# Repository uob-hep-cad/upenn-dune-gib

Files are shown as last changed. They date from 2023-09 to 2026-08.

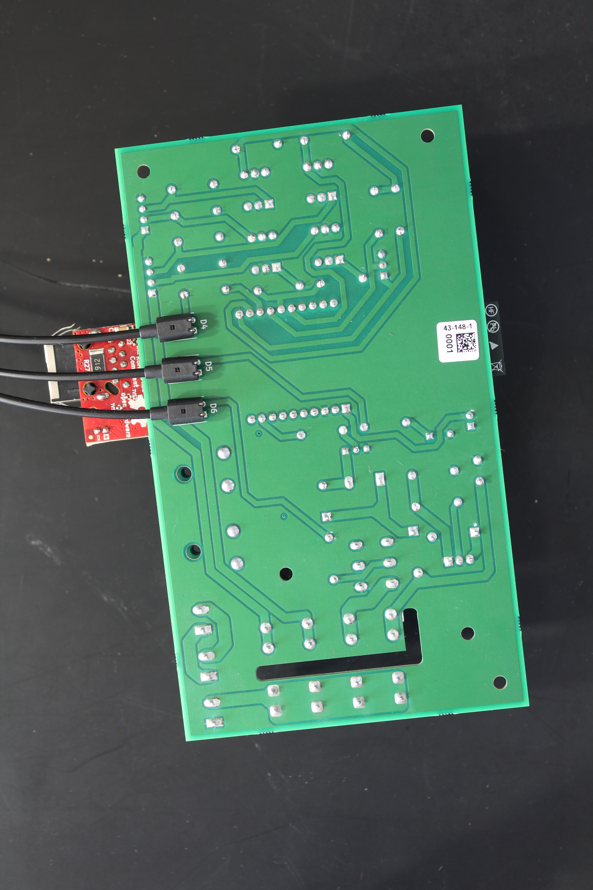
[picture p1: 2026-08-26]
PCB_Health/Photos/IMG_9404.JPG

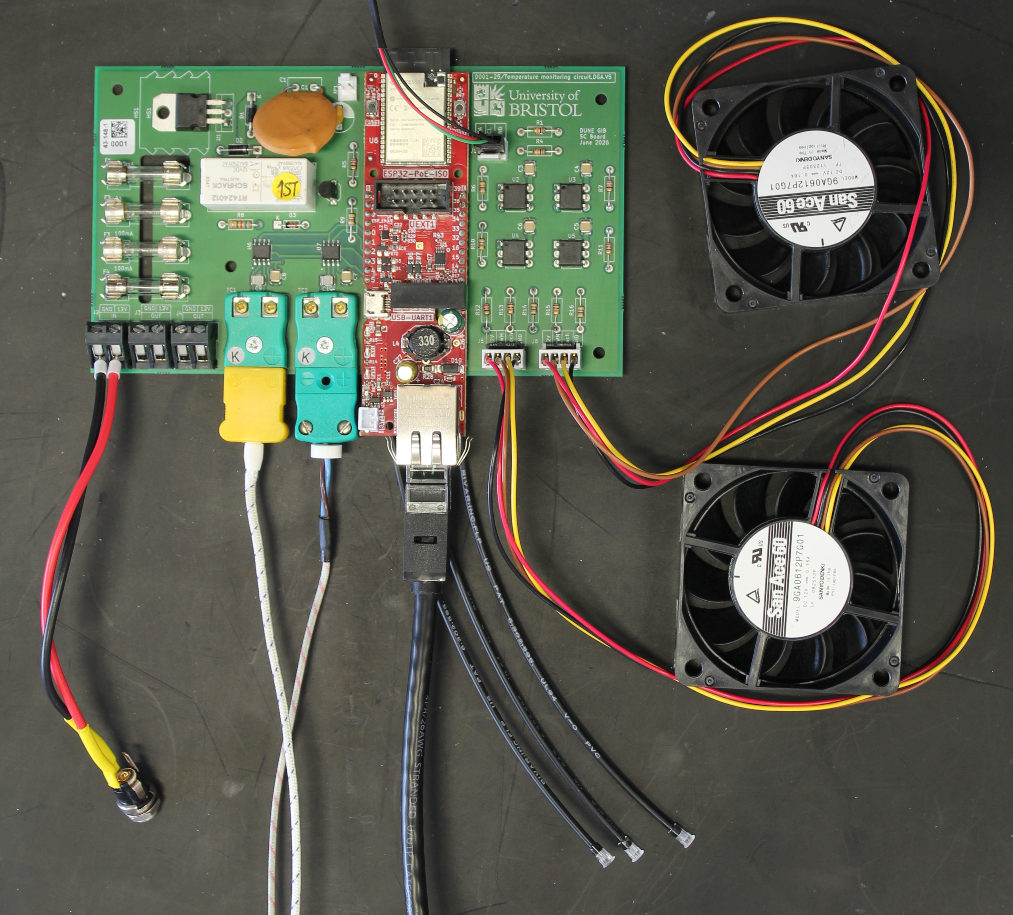
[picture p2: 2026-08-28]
PCB_Health/Photos/IMG_9411_with_cables_cropped.JPG

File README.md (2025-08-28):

# DUNE Timing System GPS Interface Board (GIB) Hardware – PCB Designs

This repository contains hardware design files for DUNE Timing System GPS Interface Board (GIB)  
It includes both Cadence Allegro and KiCAD projects for different components.

---

## 📂 Repository Structure

### `allegro/`
- Contains Cadence Allegro PCB design files.  
- Used for [describe subsystem / purpose here].

### `PCB_Health/`
- KiCAD project for a small **health monitoring board**.  
- Functions:
  - Monitor **fans** and **temperature sensors**
  - Control **power rails** 
- Supports the main GIB.

---

## 🔧 Requirements

To open and work with the files, you’ll need:

- **Cadence Allegro** (for files in `allegro/`)
- **KiCAD (≥ 6.0)** (for files in `PCB_Health/`)

---

## ⚡ Getting Started

1. Clone the repository:
   ```bash
   git clone https://github.com/uob-hep-cad/upenn-dune-gib.git
	cd upenn-dune-gib
2. For the main GIB board, open the `.opj` file with Cadence Capture CIS
3. For the PCB_Health board, open the `.kicad_pro` file with KiCAD

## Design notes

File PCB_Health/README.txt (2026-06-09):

Manufacturing files for DUNE Timing System GIB Slow Control Board
( PCB_Health.v5 )

Files produced with KiCAD 10.0

David.Cussans@bristol.ac.uk , 9/June/26
 
Directory with Gerber artwork: Gerber.D001-25.DGA.V5 
Component placement (CSV and Gerber): PCB_Health.V5-all-pos.csv PCB_Health.V5-pnp_top.gbr PCB_Health.V5-pnp_bottom.gbr

BoM: PCB_Health.V5_BOM.xlsx

4-layer board. FR4. 1.6mm  Newbury Electronics "PCB train" stack-up

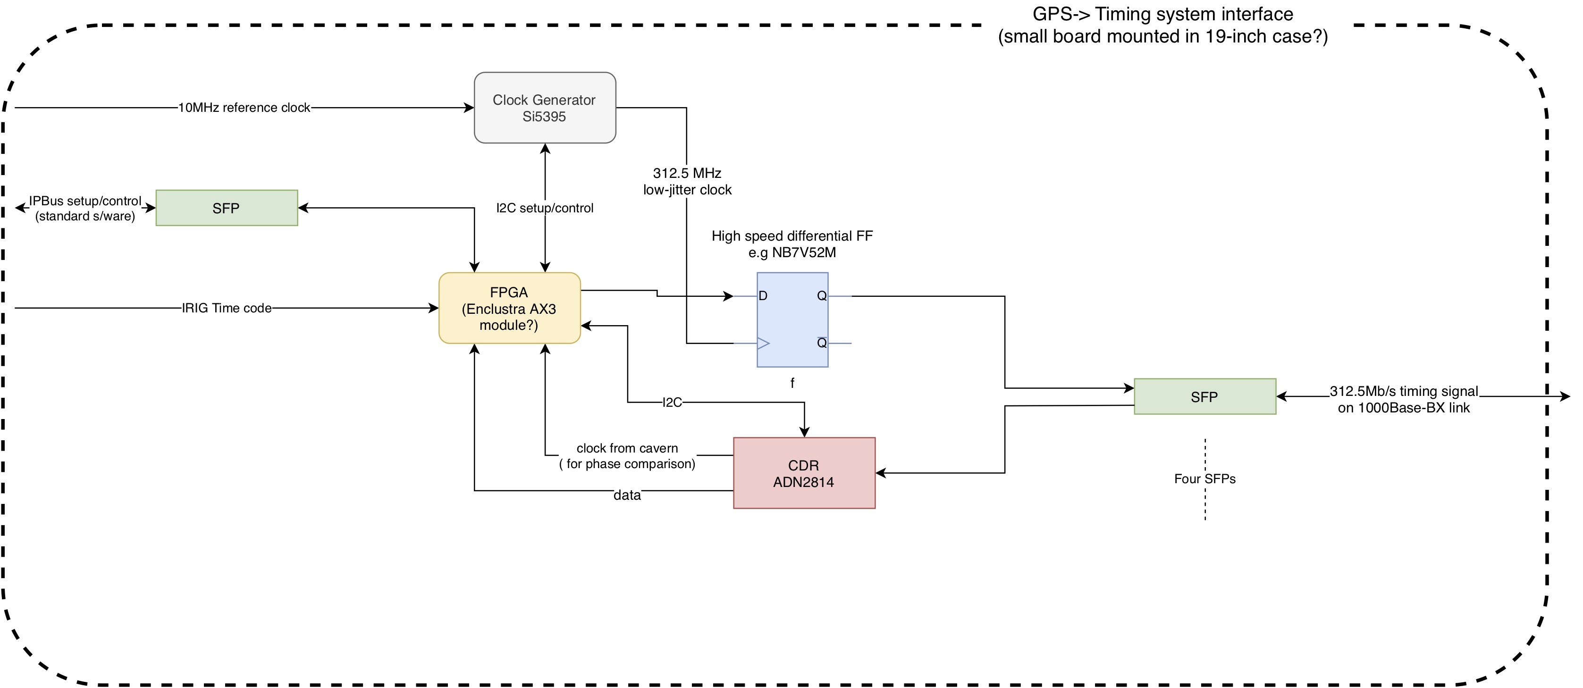
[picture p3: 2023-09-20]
Figures/GPS_timing_system_Interface.jpg

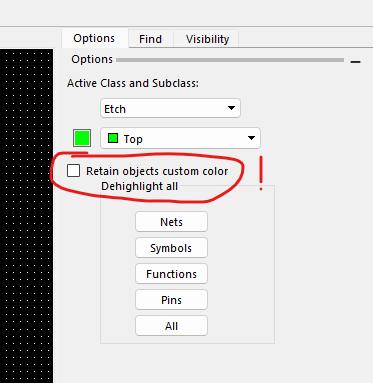
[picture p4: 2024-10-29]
Screenshot 2024-10-08 140926.png

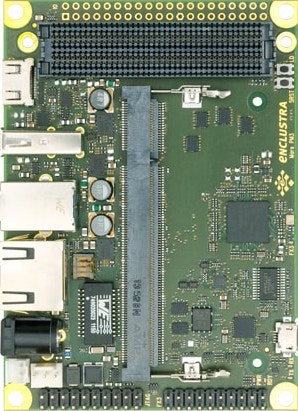
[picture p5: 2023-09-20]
Figures/mars_pm3_top.jpg

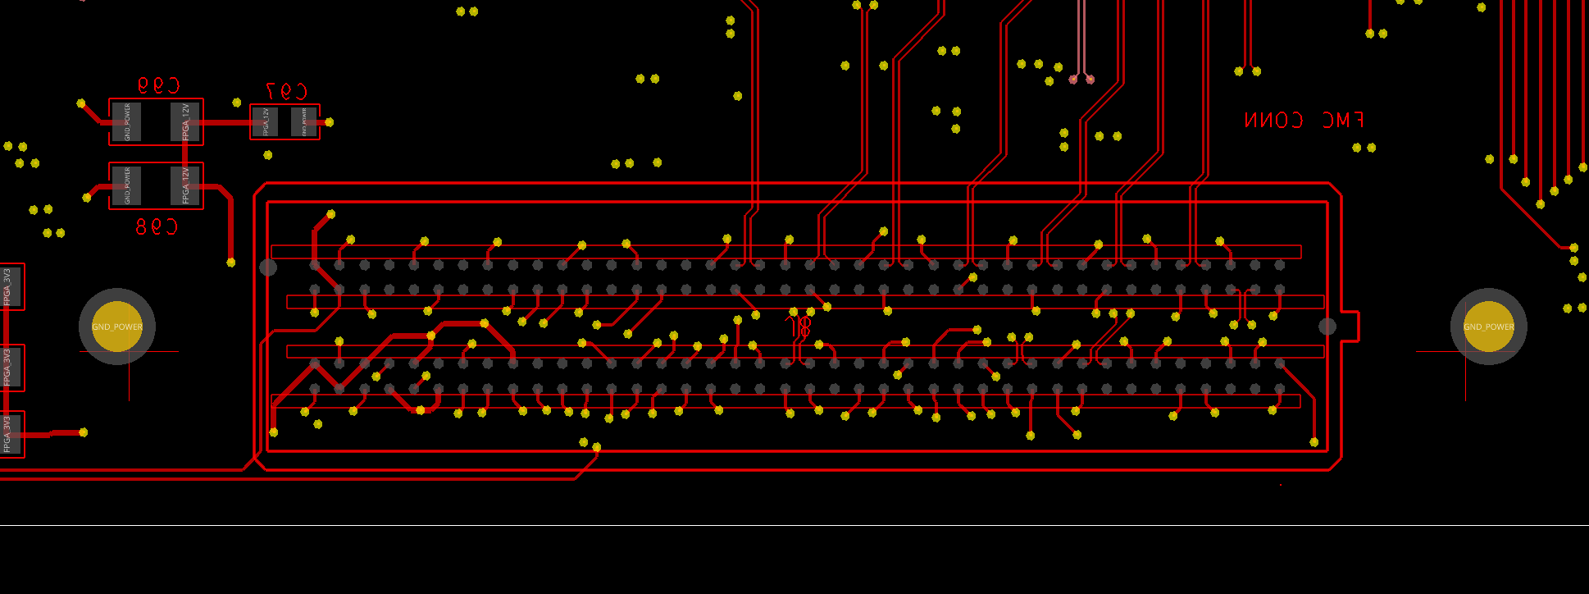
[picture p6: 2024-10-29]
Screenshot 2024-09-06 082252.png

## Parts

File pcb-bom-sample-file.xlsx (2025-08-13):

Item# | Description | Quantity | Manufacturer Name | Manufacturer Part Number | Supplier Name | Supplier Part Number | Designator | Notes
1 | CAP 1nF 16V ±5% 0201 (0603 Metric) Thickness 0.33mm SMD | 12 | Multicomp | MC0201B102K160CT | Farnell | 2320754 | C1-6, C10-15
2 | ICHAUS 3A 6CHANNEL LASER SWITCH | 3 | IC Haus | Ic-HG QFN28 | Free issued | Ic-HG QFN28 | U5, U2008, U3008
3 | 17V Input, 1A Synchronous Step-Down Converter Module in MicroSiP | 5 | Texas Instruments | TPS82150SILT | Mouser | 595-TPS82150SILT | U17, U2004, U3004-3006
Notes / colour key:
 | Quantity, Designator, Manufacturer Name, and Manufacturer Part Number columns are compulsory please.
 | Only the Manufacturer Name and Manufacturer Part Number will be used for costings and subsquent materials procurement.
 | Supplier Name and Supplier Part Number will only be used for costings and subsequent materials procurement should this be marked as critical by the client.
 | Please note that the Description field will NOT be checked during costings and subsequent materials procurement.
 | Item# / Notes column where useful / applicable. Not compulsory.
Formatting / order of columns not critical.

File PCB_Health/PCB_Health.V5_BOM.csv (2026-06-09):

Reference | Qty | Value | DNP | Exclude from BOM | Exclude from Board | Footprint | Description | Datasheet
A1 | 1 | ESP32_POE |  |  |  | ESP32:ESP32-POE-ISO-WROVER | ESP32-POE-ISO-WROVER | https://cdn-learn.adafruit.com/downloads/pdf/adafruit-huzzah32-esp32-feather.pdf
C1 | 1 | 100n |  |  |  | Capacitor_THT:C_Disc_D9.0mm_W5.0mm_P5.00mm | Capacitor THT : C Disc D9.0mm W5.0mm P5.00mm 100n
C2 | 1 | 1u |  |  |  | Capacitor_THT:CP_Radial_D8.0mm_P5.00mm | Capacitor THT : CP Radial D8.0mm P5.00mm 1u
C3,C4,C5,C6,C7,C8 | 6 | 100n |  |  |  | Capacitor_SMD:C_1210_3225Metric | Capacitor SMD : C 1210 3225Metric 100n
C9,C10 | 2 | 10n |  |  |  | Capacitor_SMD:C_1210_3225Metric | Capacitor SMD : C 1210 3225Metric 10n
D1,D2 | 2 | 1N4001 |  |  |  | Diode_THT:D_DO-41_SOD81_P10.16mm_Horizontal | Diode THT : D DO-41 SOD81 P10.16mm Horizontal 1N4001 | http://www.vishay.com/docs/88503/1n4001.pdf
D3 | 1 | 1N4148 |  |  |  | Diode_THT:D_DO-35_SOD27_P7.62mm_Horizontal | Diode THT : D DO-35 SOD27 P7.62mm Horizontal 1N4148 | https://assets.nexperia.com/documents/data-sheet/1N4148_1N4448.pdf
D4,D5,D6 | 3 | LED |  |  |  | Library:FLPR60SG | FLPR60SG
F1 | 1 | 500mA |  |  |  | Library:Littelfuse 100 Spring Brass, PCB Fuse Clip for 5 x 20 mm Cartridge Fuse | Littelfuse 100 Spring Brass, PCB Fuse Clip for 5 x 20 mm Cartridge Fuse 500mA
F2 | 1 | 2A |  |  |  | Library:Littelfuse 100 Spring Brass, PCB Fuse Clip for 5 x 20 mm Cartridge Fuse | Littelfuse 100 Spring Brass, PCB Fuse Clip for 5 x 20 mm Cartridge Fuse 2A
F3,F4 | 2 | 100mA |  |  |  | Library:Littelfuse 100 Spring Brass, PCB Fuse Clip for 5 x 20 mm Cartridge Fuse | Littelfuse 100 Spring Brass, PCB Fuse Clip for 5 x 20 mm Cartridge Fuse 100mA
H1,H2,H4,H5 | 4 | MountingHole |  |  |  | MountingHole:MountingHole_3.2mm_M3 | MountingHole : MountingHole 3.2mm M3
HS1 | 1 | Heatsink |  |  |  | Heatsink:Heatsink_AAVID_TV5G_TO220_Horizontal | Heatsink : Heatsink AAVID TV5G TO220 Horizontal
J1 | 1 | Conn_01x03_Socket |  |  |  | Connector_PinHeader_2.54mm:PinHeader_1x03_P2.54mm_Vertical | Connector PinHeader 2.54mm : PinHeader 1x03 P2.54mm Vertical
J2,J3,J4 | 3 | Conn_01x02_Socket |  |  |  | TerminalBlock:TerminalBlock_Altech_AK300-2_P5.00mm | TerminalBlock : TerminalBlock Altech AK300-2 P5.00mm
J5 | 1 | Conn_01x04_Socket |  |  |  | Library:Mole_KK_1x04__Vertical | Molex KK 1x04 Vertical
J6 | 1 | Conn_01x04_Socket |  |  |  | Connector_PinHeader_2.54mm:PinHeader_1x04_P2.54mm_Vertical | Connector PinHeader 2.54mm : PinHeader 1x04 P2.54mm Vertical
JP1 | 1 | Jumper_2_Open |  |  |  | Connector_PinHeader_2.54mm:PinHeader_1x02_P2.54mm_Vertical | Connector PinHeader 2.54mm : PinHeader 1x02 P2.54mm Vertical
K1 | 1 | RT424012 |  |  |  | Relay_THT:Relay_DPDT_Schrack-RT2-FormC_RM5mm | Relay THT : Relay DPDT Schrack-RT2-FormC RM 5mm | http://www.te.com/commerce/DocumentDelivery/DDEController?Action=showdoc
Q1 | 1 | BC337 |  |  |  | Package_TO_SOT_THT:TO-92_Inline_Wide | Package TO SOT THT : TO-92 Inline Wide BC337 | https://diotec.com/tl_files/diotec/files/pdf/datasheets/bc337.pdf
R1,R4,R13,R15 | 4 | 10k |  |  |  | Library:R_Axial_DIN0207_L6.3mm_D2.5mm_P10.16mm_Horizontal | R Axial DIN0207 L6.3mm D2.5mm P10.16mm Horizontal 10k
R2 | 1 | 220 |  |  |  | Library:R_Axial_DIN0207_L6.3mm_D2.5mm_P10.16mm_Horizontal | R Axial DIN0207 L6.3mm D2.5mm P10.16mm Horizontal
R3 | 1 | 680 |  |  |  | Library:R_Axial_DIN0207_L6.3mm_D2.5mm_P10.16mm_Horizontal | R Axial DIN0207 L6.3mm D2.5mm P10.16mm Horizontal
R5,R7,R11,R12 | 4 | 270 |  |  |  | Library:R_Axial_DIN0207_L6.3mm_D2.5mm_P10.16mm_Horizontal | R Axial DIN0207 L6.3mm D2.5mm P10.16mm Horizontal
R6,R9,R10,R14,R16 | 5 | 470 |  |  |  | Library:R_Axial_DIN0207_L6.3mm_D2.5mm_P10.16mm_Horizontal | R Axial DIN0207 L6.3mm D2.5mm P10.16mm Horizontal
R8 | 1 | 620 |  |  |  | Library:R_Axial_DIN0207_L6.3mm_D2.5mm_P10.16mm_Horizontal | R Axial DIN0207 L6.3mm D2.5mm P10.16mm Horizontal
TC1,TC2 | 2 | Thermocouple_Alt |  |  |  | Connector Thermo:Thermocouple Connector | Connector Thermo : Thermocouple Connector
U1 | 1 | LM317_TO-220 |  |  |  | Package_TO_SOT_THT:TO-220-3_Vertical | Package TO SOT THT : TO-220-3 Vertical | http://www.ti.com/lit/ds/symlink/lm317.pdf
U2,U3,U4,U5 | 4 | H11L1 |  |  |  | Library:DIP-6_W7.62mm | DIP-6 W7.62mm | https://www.onsemi.com/pub/Collateral/H11L3M-D.PDF
U6,U7 | 2 | MAX6675ISA_ |  |  |  | MAX6675ISA_:SOIC127P600X175-8N | MAX6675ISA : SOIC127P600X175-8N

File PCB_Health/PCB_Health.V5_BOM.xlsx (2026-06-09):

Description | Qty per BOM | Quantity per batch | Min Quantity to order | Manufacturer | Manufacturer Part Number | Supplier | Supplier Part Number | Designator | Package Type | Technology | Comment | Status | Original Manufacturer Part No from client BOM
ESP32-POE IOT EVAL BOARD | 1 | 2 | 2 | Olimex LTD | ESP32-POE-ISO-WROVER | DIGIKEY | 1188-ESP32-POE-ISO-WROVER-ND | A1 | Bulk | THT |  | Found | ESP32_POE
CAP CER 0.1UF 500V Z5V RADIAL | 7 | 14 | 14 | Vishay Beyschlag/Draloric/BC Components | S104Z93Z5VL83L0R | DIGIKEY | BC5183-ND | C1,C3,C4,C5,C6,C7,C8 | Bulk | THT |  | Found | 100n
CAP TANT 1UF 10% 25V RADIAL | 1 | 2 | 2 | KEMET | T356A105K025AT | DIGIKEY | 399-3603-ND | C2 | Bulk | THT |  | Found | 1u
YAGEO - CC1210FKNPO9BN103 - SMD Multilayer Ceramic Capacitor, 0.01 µF, 50 V, 1210 [3225 Metric], ± 1%, C0G / NP0 | 2 | 4 | 5 | YAGEO | CC1210FKNPO9BN103 | FARNELL | 4255887 | C9,C10 | Cut Tape | SMD |  | Found | 10n
MULTICOMP PRO - 1N4001. - DIODE, STANDARD RECOVERY, 1A, 50V, DO-204AL-2 | 2 | 4 | 5 | MULTICOMP PRO | 1N4001. | FARNELL | 2306346 | D1,D2 | Cut Tape | THT |  | Found | 1N4001
MULTICOMP PRO - 1N4148. - DIODE, ULTRAFAST RECOVERY, 150mA, 75V, DO-204AH-2 | 1 | 2 | 5 | MULTICOMP PRO | 1N4148. | FARNELL | 2306361 | D3 | Cut Tape | THT |  | Found | 1N4148
LED CBI 3MM GRN THROUGH HOLE | 3 | 6 | 6 | Bivar Inc. | FLPR6.0-SG | DIGIKEY | 492-1201-ND | D4,D5,D6 | Bag | THT |  | Found | LED
FUSE CLIP CARTRIDGE 250V 10A PCB | 1 | 2 | 2 | Littelfuse Inc. | 01000056Z | DIGIKEY | F3784-ND | F1 | Bulk | THT |  | Found | 500mA
FUSE CLIP CARTRIDGE 250V 10A PCB | 1 | 2 | 2 | Littelfuse Inc. | 01000056Z | DIGIKEY | F3784-ND | F2 | Bulk | THT |  | Found | 2A
FUSE CLIP CARTRIDGE 250V 10A PCB | 2 | 4 | 4 | Littelfuse Inc. | 01000056Z | DIGIKEY | F3784-ND | F3,F4 | Bulk | THT |  | Found | 100mA
BOYD - TV5G - Heat Sink, PCB, Board Level, 21.6 °C/W, TO-126, 22 mm, 19 mm, 19 mm | 1 | 2 | 2 | BOYD | TV5G | FARNELL | 170072 | HS1 | Each | UNMOUNTED |  | Found | Heatsink
Headers & Wire Housings 3C STR HEADER W/FRLK | 1 | 2 | 2 | Molex | 22-27-2031 | MOUSER | 538-22-27-2031 | J1 | Standard Pack Qty | THT |  | Found | Conn_01x03_Socket
Fixed Terminal Blocks AK300/2 PC 45DegGry | 3 | 6 | 6 | Altech | 30.602 | MOUSER | 845-30.602 | J2,J3,J4 | Standard Pack Qty | THT |  | Found | Conn_01x02_Socket
MOLEX - 171856-4004 - Pin Header, Black, Board-to-Board, Power, Signal, Wire-to-Board, 2.54 mm, 1 Rows, 4 Contacts | 2 | 4 | 4 | MOLEX | 171856-4004 | FARNELL | 4667772 | J5,J6 | Cut Tape | THT |  | Found | Conn_01x04_Socket
Conn Wire to Board HDR 2 POS 2.54mm Solder ST Top Entry Thru-Hole KK Bag | 1 | 2 | 2 | Molex | 0022232021 | ARROW | 0323_00039992 | JP1 | BAG | THT |  | Found | Jumper_2_Open
Power Relay 12VDC 8A DPDT(29x12.7x15.7)mm THT | 1 | 2 | 2 | TE Connectivity | RT424012 | ARROW | 0323_00028596 | K1 | BOX | THT |  | Found | RT424012
MULTICOMP PRO - BC337 - Bipolar (BJT) Single Transistor, NPN, 45 V, 800 mA, 625 mW, TO-92, Through Hole | 1 | 2 | 5 | MULTICOMP PRO | BC337 | FARNELL | 1574379 | Q1 | Each | THT |  | Found | BC337
MULTICOMP PRO - MCRE000049 - Through Hole Resistor, 10 kohm, MC CFR Series, 125 mW, ± 5%, Axial Leaded, 200 V | 4 | 8 | 8 | MULTICOMP PRO | MCRE000049 | FARNELL | 1700251 | R1,R4,R13,R15 | Each | THT |  | Found | 10k
MULTICOMP PRO - MCRE000029 - Through Hole Resistor, 220 ohm, MC CFR Series, 125 mW, ± 5%, Axial Leaded, 200 V | 1 | 2 | 5 | MULTICOMP PRO | MCRE000029 | FARNELL | 1700228 | R2 | Each | THT |  | Found | 220
MULTICOMP PRO - MCRE000035 - Through Hole Resistor, 680 ohm, MC CFR Series, 125 mW, ± 5%, Axial Leaded, 200 V | 1 | 2 | 5 | MULTICOMP PRO | MCRE000035 | FARNELL | 1700234 | R3 | Each | THT |  | Found | 680
MULTICOMP PRO - MCRE000030 - Through Hole Resistor, 270 ohm, MC CFR Series, 125 mW, ± 5%, Axial Leaded, 200 V | 4 | 8 | 8 | MULTICOMP PRO | MCRE000030 | FARNELL | 1700229 | R5,R7,R11,R12 | Each | THT |  | Found | 270
MULTICOMP PRO - MCRE000033 - Through Hole Resistor, 470 ohm, MC CFR Series, 125 mW, ± 5%, Axial Leaded, 200 V | 5 | 10 | 10 | MULTICOMP PRO | MCRE000033 | FARNELL | 1700232 | R6,R9,R10,R14,R16 | Each | THT |  | Found | 470
RES 620 OHM 5% 1/4W AXIAL | 1 | 2 | 2 | KOA Speer Electronics, Inc. | CF1/4CT52R621J | DIGIKEY | 2019-CF1/4CT52R621JCT-ND | R8 | Cut Tape (CT) | THT |  | Found | 620
LABFACILITY - IM-K-PCB - Thermocouple Connector, Miniature, Green, Socket, Type K, IEC, PCB Mount | 2 | 4 | 4 | LABFACILITY | IM-K-PCB | FARNELL | 3810628 | TC1,TC2 | Each | THT |  | Found | Thermocouple_Alt
Standard Regulator Pos 1.2V to 37V 0.4A 3-Pin(3+Tab) TO-220AB Tube | 1 | 2 | 2 | STMicroelectronics | LM317T | ARROW | 0323_00031097 | U1 | RAIL | THT |  | Found | LM317_TO-220
Optocoupler Logic-Out DC-IN 1-CH 6-Pin DIP | 4 | 8 | 8 | Everlight Electronics | H11L1 | ARROW | 0323_02418914 | U2,U3,U4,U5 | BULK | THT |  | Found | H11L1
ANALOG DEVICES - MAX6675ISA+ - Temperature Sensor IC, Digital, ± 3°C, 0 °C, 1024 °C, NSOIC, 8 Pins | 2 | 4 | 4 | ANALOG DEVICES | MAX6675ISA+ | FARNELL | 2518704 | U6,U7 | Each | SMD |  | Found | MAX6675ISA_

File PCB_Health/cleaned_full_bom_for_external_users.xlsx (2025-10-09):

Description | Qty per BOM | Quantity per batch | Min Quantity to order | Manufacturer | Manufacturer Part Number | Supplier | Supplier Part Number | Designator | Package Type | Technology | Comment | Status | Original Manufacturer Part No from client BOM
WiFi Development Tools - 802.11 ESP32-POE-ISO IoT development board with 100Mb Ethernet, Power over Ethernet, WiFi, BLE, programmer | 1 | 2 | 2 | Olimex Ltd. | ESP32-POE-ISO-WROVER | MOUSER | 909-P32POEISOWROVER | A1 | Standard Pack Qty | THT | ESP32_POE | Found | ESP32-POE-ISO-WROVER
Multilayer Ceramic Capacitors MLCC - SMD/SMT WCAP-CSGP 0.01uF 1210 5% 50V MLCC | 2 | 4 | 4 | Wurth Elektronik | 885012009023 | MOUSER | 710-885012009023 | C1,C2 | Cut Tape | SMD | 10n | Found | 885012009023
CAP CER 0.1UF 50V X7R 0805 | 7 | 14 | 14 | KEMET | C0805C104K5RACTU | DIGIKEY | 399-C0805C104K5RACTUCT-ND | C3,C4,C5,C6,C7,C8,C9 | Cut Tape (CT) | SMD | 100n | Found | C0805C104K5RACTU
Aluminium Electrolytic Capacitors - Radial Leaded 1.0UF 250V ELECT NHG RADIAL | 1 | 2 | 2 | Panasonic | ECA-2EHG010 | MOUSER | 667-ECA-2EHG010 | C10 | Standard Pack Qty | SMD | 1u | Found | ECA2EHG010
MULTICOMP PRO - 1N4001. - DIODE, STANDARD RECOVERY, 1A, 50V, DO-204AL-2 | 2 | 4 | 5 | MULTICOMP PRO | 1N4001. | FARNELL | 2306346 | D1,D2 | Cut Tape | THT | 1N4001 | Found | 1N4001-E3/54
PCB MNT FUSEHOLDER 5X20MM | 4 | 8 | 8 | BULGIN LTD | FX0457 | ANGLIA | 138857001 | F1,F2,F3,F4 | Bag | SMD | 500mA | Found | FX0457
Screws & Fasteners PEEK SOCKET HEAD SCREW M3 X 10 | 1 | 2 | 2 | Essentra | 183031070409 | MOUSER | 144-183031070409 | H1 | Standard Pack Qty | UNMOUNTED | Heatsink fixing | Found
BOYD - TV5G - Heat Sink, PCB, Board Level, 21.6 °C/W, TO-126, 22 mm, 19 mm, 19 mm | 1 | 2 | 2 | BOYD | TV5G | FARNELL | 170072 | HS1 | Each | SMD | Heatsink | Found | TV5G
TERMINAL BLOCK 2W | 3 | 6 | 6 | CAMDENBOSS | CTB0502/2 | ANGLIA | 1041430001 | J1,J2,J5 | Bag | THT | Conn_01x02_Socket | Found | 897-0843
Conn Wire to Board HDR 4 POS 2.54mm Solder ST Top Entry Thru-Hole KK Bag | 2 | 4 | 4 | Molex | 0022292041 | ARROW | 0323_00030517 | J3,J4 | BAG | THT | Conn_01x04_Socket | Found | 22-29-2041
Conn Wire to Board HDR 3 POS 2.54mm Solder ST Top Entry Thru-Hole KK Bag | 1 | 2 | 2 | Molex | 0022272031 | ARROW | 0323_00036827 | J6 | BAG | THT | Conn_01x03_Pin | Found | 22-27-2031
Relay: electromagnetic; DPDT; Ucoil: 12VDC; 8A; 8A/250VAC; 8A/30VDC | 1 | 2 | 2 | TE Connectivity | RT424012 | TME | RT424012 | K1 |  | THT | RT424012 | Found | RT424012
TO92 45V 0.8A 0.625W NPN | 1 | 2 | 1000 | INVAC | BC337-25 | ANGLIA | 1517347001 | Q1 | Bag | THT | BC337 | Found | BC337-25 A1
Metal Film Resistors - Through Hole 470 OHM 1/4W 1% | 5 | 10 | 10 | YAGEO | MFR-25FTE52-470R | MOUSER | 603-MFR-25FTE52-470R | R1,R3,R5,R7,R8 | Standard Pack Qty | THT | 470 | Found | MFR-25FTE52-470R
RES 270 OHM 1% 1/4W AXIAL | 4 | 8 | 8 | YAGEO | MFR-25FTE52-270R | DIGIKEY | 13-MFR-25FTE52-270RCT-ND | R2,R4,R6,R9 | Cut Tape (CT) | THT | 270 | Found | MFR-25FTE52-270R
RES 680 OHM 1% 0.6W AXIAL | 1 | 2 | 2 | TE Connectivity Passive Product | LR1F680R | DIGIKEY | A105963CT-ND | R11 | Cut Tape (CT) | SMD | 680 | Found | LR1F680R
IEC TYPE K PCB SOCKET IM-K-PCB | 2 | 4 | 4 | Labfacility Ltd | XE-1109-001 | DIGIKEY | 5425-XE-1109-001-ND | TC1,TC2 | Bag | THT | Thermocouple_Alt | Found | 304-14-320
Optocoupler Logic-Out DC-IN 1-CH 6-Pin DIP | 4 | 8 | 8 | Everlight Electronics | H11L1 | ARROW | 0323_02418914 | U1,U4,U5,U7 | BULK | SMD | H11L1 | Found | H11L1
ANALOG DEVICES - MAX6675ISA+ - Temperature Sensor IC, Digital, ± 3°C, 0 °C, 1024 °C, NSOIC, 8 Pins | 2 | 4 | 4 | ANALOG DEVICES | MAX6675ISA+ | FARNELL | 2518704 | U2,U3 | Each | SMD | MAX6675ISA_ | Found | MAX6675ISA+
IC: voltage regulator; linear,adjustable; 1.2÷37V; 1.5A; TO220-3 | 1 | 2 | 2 | TEXAS INSTRUMENTS | LM317T/NOPB | TME | LM317T/NOPB | U6 |  | THT | LM317_TO-220 | Found | LM317T/NOPB
RES 220 OHM 1% 1/4W AXIAL | 1 | 2 | 2 | YAGEO | MFR-25FTE52-220R | DIGIKEY | 13-MFR-25FTE52-220RCT-ND | R10 | Cut Tape (CT) | THT |  | Found

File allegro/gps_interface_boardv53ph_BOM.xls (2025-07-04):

Quantity | Designator | Description | Manufacturer | Manufacturer Part Number | Supplier 1 | Supplier Part Number 1 | Notes
3 | J27, J28, J29 | KK 0.1in 3 way latching | Molex | 22-23-2031
1 | J300 | Power to the Board MiniFitJr | Molex | 172448-0004
1 | U100 | Switching Voltage Regulator | Analog Devices | LTM8029IYPBF
2 | C1, C3 | 10nF 16V X7R 0402 | Samsung Electronic | CL05B103JO5NNWC |  |  | Can be alternative but match OR exceed dielectric/volt rating | 0.01UF
47 | C14, C15, C18, C19, C20, C23, C24, C25, C26, C27, C28, C34, C35, C36, C37, C38, C39, C108, C109, C110, C111, C112, C113, C128, C129, C140, C141, C163, C164, C186, C187, C209, C210, C232, C233, C255, C256, C272, C276, C277, C2711, C2733, C2734, C2735, C2736, C2737, C2738 | 100nF 16V X7R 0402 | Kemet | C0402C104J4RAC7411 |  |  | Can be alternative but match OR exceed dielectric/volt rating | 0.1UF
1 | C127 | 4.7uF 16V X5R 0402 | KYOCERA AVX | 0402YD475MAT2A |  |  | Can be alternative but match OR exceed dielectric/volt rating | 4.7UF
1 | C2732 | 470nF 16V X7S 0402 | TDK | CGA2B1X7S1C474K050BE |  |  | Can be alternative but match OR exceed dielectric/volt rating | 0.47UF
76 | C5, C6, C8, C11, C53, C54, C56, C58, C59, C60, C62, C64, C69, C71, C72, C74, C75, C78, C79, C83, C84, C86, C115, C116, C117, C119, C123, C132, C133, C135, C136, C138, C155, C156, C158, C159, C161, C178, C179, C181, C182, C184, C201, C202, C204, C205, C207, C224, C225, C227, C228, C230, C247, C248, C250, C251, C253, C270, C271, C2660, C2670, C2690, C2712, C2713, C2714, C2718, C2722, C2723, C2724, C2725, C2726, C2739, C2740, C2741, C2742, C2750 | 100nF 50V X7R 0603 | KYOCERA AVX | KAM15AR71H104KM |  |  | Can be alternative but match OR exceed dielectric/volt rating | 0.1UF
9 | C7, C9, C10, C12, C13, C16, C21, C22, C29 | 10uF 16V X6S 0603 | Murata | GRM188C81C106MA73D |  |  | Can be alternative but match OR exceed dielectric/volt rating | 10UF
8 | C17, C41, C42, C87, C3712, C3713, C3714, C3715 | 1uF 16V X6S 0603 | Murata | GRT188C81C105KE13D |  |  | Can be alternative but match OR exceed dielectric/volt rating | 1UF
2 | C43, C44 | 470nF 16V X7R 0603 | Kemet | C0603C474K4RACTM |  |  | Can be alternative but match OR exceed dielectric/volt rating | 0.47UF
1 | C51 | 5pF 50V C0G 0603 | KYOCERA AVX | 06035A5R0DAT2A |  |  | Can be alternative but match OR exceed dielectric/volt rating | 5.0PF
5 | C57, C65, C76, C85, C2710 | 10nF 16V X7R 0603 | Vishay | VJ0603Y103KXJAC31X |  |  | Can be alternative but match OR exceed dielectric/volt rating | 0.01UF
18 | C139, C162, C185, C208, C231, C254, C2727, C2728, C2729, C2730, C2731, C2743, C2744, C2745, C2746, C2747, C2748, C2749 | 1nF 16V X7R 0603 | KYOCERA AVX | 0603YC102KAT2A |  |  | Can be alternative but match OR exceed dielectric/volt rating | 1000PF
2 | C274, C275 | 4.7uF 16V X7R 0603 | Murata | GRM188Z71C475KE21D |  |  | Can be alternative but match OR exceed dielectric/volt rating | 4.7UF
1 | C40 | 10uF 16V X7R 0805 | TAIYO YUDEN | EMK212BB7106KG-T |  |  | Can be alternative but match OR exceed dielectric/volt rating | 10UF
12 | C49, C50, C52, C55, C61, C63, C70, C73, C77, C80, C2650, C2680 | 47uF 10V X5R 0805 | Murata | GRM21BR61A476ME15L |  |  | Can be alternative but match OR exceed dielectric/volt rating | 47UF
4 | C97, C100, C101, C105 | 100nF 50V X7R 0805 | KYOCERA AVX | 08055C104K4Z4A |  |  | Can be alternative but match OR exceed dielectric/volt rating | 0.1UF
14 | C134, C137, C157, C160, C180, C183, C203, C206, C226, C229, C249, C252, C2717, C2719 | 22uF 16V X5R 0805 | TDK | C2012X5R1C226K125AC |  |  | Can be alternative but match OR exceed dielectric/volt rating | 22UF
6 | L1, L2, L3, L5, L19, L22 | Ferrite Bead 120ohms 100MHz | Laird | LI0805H121R-10 |  |  | Can be alternative but match OR exceed dielectric/volt rating | 120 Ohm@100MHz
1 | C88 | 22uF 16V X7R 1206 | TAIYO YUDEN | EMK316BB7226ML-T |  |  | Can be alternative but match OR exceed dielectric/volt rating | 22UF
7 | C98, C99, C102, C103, C104, C106, C107 | 47uF 16V X5R 1206 | Murata | GRM31CR61C476ME44L |  |  | Can be alternative but match OR exceed dielectric/volt rating | 47UF
1 | F1 | High Inrush Current Withstand, 1206, 30A | Bourns | SF-1206HI400M-2 |  |  |  | 4A
1 | F2 | 1A 1206 Fuse | MultiComp | MP001606 |  |  |  | 0.75A
4 | C66, C67, C81, C82 | 100uF 16V X5R 1210 | Kemet | C1210C107M4PACTU |  |  | Can be alternative but match OR exceed dielectric/volt rating | 100UF
14 | L7, L8, L9, L10, L11, L12, L13, L14, L15, L16, L17, L18, L20, L21 | 4.7 µH, 1.5 ohm, 55 MHz, 220 mA, 1210 | Bourns | CM322522-4R7KL |  |  |  | 4.7 uH
1 | U6 | Switching Voltage Regulator | Analog Devices | LT8645SJV-2
1 | U1 | Clock Buffer | Analog Devices | LTC6957IDD-2#PBF
1 | U15 | Supervisory Circuit | Texas Instruments | TPS3895ADRYR
1 | FL1 | Choke Surface Mount 500 Ohms @ 100 MHz | Murata | DLW5BTM501SQ2L
4 | J11, J12, J15, J16 | 0.1in Pitch 2 pin header | Tyco Connectivity | 826926-2
10 | D1, D15, D17, D21, D25, D29, D33, D37, D41, D43 | Red 0603 LED | LiteOn | LTST-C193KRKT-5A
15 | D2, D4, D5, D6, D7, D8, D14, D16, D20, D24, D28, D32, D36, D40, D42 | Green 0603 LED | LiteOn | LTST-C193KGKT-5A
6 | U22, U26, U30, U34, U38, U42 | Flip-Flops | OnSemi | NB7V52MMNG
3 | U8, U10, U13 | Current & Power Monitors | Analog Devices | LTC2945CUD
5 | U7, U9, U11, U12, U101 | LDO Voltage Regulator High-Current | Texas Instruments | TPS7A8500RGRT
1 | U107 | (D)Encoders, (De)Multiplexers 4.25Gbps | Microchip | SY58608UMG
1 | U104 | Timer | Analog Devices | ADN2814ACPZ
1 | U48 | Clock Synthesizer/Jitter Cleaner | Skyworks | SI5395A-A-GM
2 | Y1, Y2 | MEMS OSC TCXO 50.0000MHZ LVDS | SiTime | SIT5021AI-2DE-25E-50.000000X
1 | P2 | 20 way 0.1in dual row | TE Connectivity | 1-826632-0
1 | P1 | 12 way 0.1in dual row | TE Connectivity | 5-146256-6
19 | R1, R10, R19, R20, R21, R22, R23, R24, R25, R26, R81, R82, R106, R107, R110, R111, R254, R2670, R2694 | 1K 0402 Resistor | Panasonic | ERJ-2RKF1001X |  |  | Can be alternative but 1% if possible | 1k
13 | R31, R35, R131, R152, R173, R194, R215, R236, R1540, R2683, R2689, R2692, R2693, R265 | 100R 0402 Resistor | Panasonic | ERJ-2RKF1000X |  |  | Can be alternative but 1% if possible | 100
28 | R48, R49, R59, R60, R63, R64, R65, R70, R112, R113, R114, R115, R118, R247, R248, R249, R250, R255, R256, R257, R259, R262, R263, R2662, R2665, R2666, R2686, R2687 | 0R 0402 Resistor | Panasonic | ERJ-U020R00X |  |  | Can be alternative but 1% if possible | 0
1 | R78 | 97.6K 0402 Resistor | Panasonic | ERJ-2RKF9762X |  |  | Can be alternative but 1% if possible | 97.6k
1 | R79 | 20K 0402 Resistor | Panasonic | ERJ-2RKF2002X |  |  | Can be alternative but 1% if possible | 20k
3 | R93, R94, R95 | 4.99K 0402 Resistor | Panasonic | ERJ-2RKF4991X |  |  | Can be alternative but 1% if possible | 4.99k
12 | R121, R122, R142, R143, R163, R164, R184, R185, R205, R206, R226, R227 | 6.81K 0402 Resistor | Panasonic | ERJ-2RKF6811X |  |  | Can be alternative but 1% if possible | 6.81k
12 | R123, R126, R144, R147, R165, R168, R186, R189, R207, R210, R228, R231 | 3.83K 0402 Resistor | Panasonic | ERJ-2RKF3831X |  |  | Can be alternative but 1% if possible | 3.83K
29 | R124, R125, R127, R129, R145, R146, R148, R150, R166, R167, R169, R171, R187, R188, R190, R192, R208, R209, R211, R213, R229, R230, R232, R234, R2676, R2677, R2679, R2681, R2688 | 4.7K 0402 Resistor | Panasonic | ERJ-2RKF4701X |  |  | Can be alternative but 1% if possible | 4.7k
3 | R264, R267, R268 | 49.9R 0402 Resistor | Panasonic | ERJ-2RKF49R9X |  |  | Can be alternative but 1% if possible | 49.9
1 | R2650 | 280K 0402 Resistor | Panasonic | ERJ-2RKF2802X |  |  | Can be alternative but 1% if possible | 280 kOhm
2 | R2, R4 | 24.9R 0603 Resistor | Panasonic | ERJ-PA3F24R9V |  |  | Can be alternative but 1% if possible | 24.9 Ohm
5 | R9, R71, R72, R73, R253 | 0R 0603 Resistor | Panasonic | ERJ-3GEY0R00V |  |  | Can be alternative but 1% if possible | 0 Ohm
4 | R11, R12, R15, R16 | 133R 0603 Resistor | Panasonic | ERJ-PA3F1330V |  |  | Can be alternative but 1% if possible | 133
4 | R13, R14, R17, R18 | 68R 0603 Resistor | Panasonic | ERJ-PA3F68R0V |  |  | Can be alternative but 1% if possible | 68
2 | R32, R34 | 75R 0603 Resistor | Panasonic | ERJ-PA3F75R0V |  |  | Can be alternative but 1% if possible | 75 Ohm
1 | R33 | 1K 0603 Resistor | Panasonic | ERJ-PA3F1001V |  |  | Can be alternative but 1% if possible | 1k
1 | R36 | 390K 0603 Resistor | Panasonic | ERJ-PA3F3903V |  |  | Can be alternative but 1% if possible | 390 kOhm
18 | R38, R40, R50, R56, R61, R128, R130, R149, R151, R170, R172, R191, R193, R212, R214, R233, R235, R2660 | 4.99K 0603 Resistor | Panasonic | ERJ-PA3F4992V |  |  | Can be alternative but 1% if possible | 4.99K
1 | R41 | 1M 0603 Resistor | Panasonic | ERJ-PA3F1004V |  |  | Can be alternative but 1% if possible | 1M
1 | R42 | 17.8K 0603 Resistor | Panasonic | ERJ-PA3F1782V |  |  | Can be alternative but 1% if possible | 17.8k
1 | R46 | 12.1K 0603 Resistor | Panasonic | ERJ-PA3F1212V |  |  | Can be alternative but 1% if possible | 12.1K
1 | R47 | 2.32K 0603 Resistor | Panasonic | ERJ-PA3F2321V |  |  | Can be alternative but 1% if possible | 2.32k
22 | R83, R84, R85, R86, R87, R88, R89, R90, R91, R92, R96, R97, R98, R99, R100, R101, R102, R103, R245, R246, R251, R252 | 4.7K 0603 Resistor | Panasonic | ERJ-PA3F4701V |  |  | Can be alternative but 1% if possible | 4.7K
16 | R104, R105, R108, R109, R119, R120, R140, R141, R161, R162, R182, R183, R203, R204, R224, R225 | 49.9R 0603 Resistor | Panasonic | ERJ-PA3F49R9V |  |  | Can be alternative but 1% if possible | 49.9 Ohm
1 | R116 | 100R 0603 Resistor | Panasonic | ERJ-PA3F1000V |  |  | Can be alternative but 1% if possible | 100
17 | R117, R132, R133, R153, R154, R174, R175, R195, R196, R216, R217, R237, R238, R2684, R2685, R2690, R2691 | 200R 0603 Resistor | Panasonic | ERJ-PA3F2000V |  |  | Can be alternative but 1% if possible | 200
1 | R2640 | 143K 0603 Resistor | Panasonic | ERJ-PA3F1433V |  |  | Can be alternative but 1% if possible | 143K
9 | R37, R39, R43, R44, R51, R57, R62, R74, R80 | 75R 0805 Resistor | Panasonic | ERJ-P06F75R0V |  |  | Can be alternative but 1% if possible | 75 Ohm
1 | R45 | 0.005R 0805 Resistor | Bourns | CRF0805-FZ-R005ELF |  |  | Can be alternative but 1% if possible
4 | R52, R54, R2667, R2668 | 0.0047R 0805 Resistor | Panasonic | ERJ-6BWFR047V
2 | R53, R58 | 0.02R 0805 Resistor | Yageo | PE0805FRF470R02L
1 | J8 | Board to Board & Mezzanine Connector | Samtec | ASP-134606-01
1 | U46 | Board Mount Temperature Sensor | Texas Instruments | LM75AIMX/NOPB
1 | U49 | EEPROM 2K 256 X 8 | Microchip | 24AA025E48T-I/SN
1 | U102 | LDO Voltage Regulator | Texas Instruments | TPS74618PQWDRBRQ1
3 | IC1, IC2, U47 | Translation - Voltage Levels Dual Bit | Texas Instruments | SN74LVC2T45DCUR
2 | U52, U53 | I/O Expander | Texas Instruments | TCA9539PWR
1 | U17 | 4-bit Bidirectional Voltage-Level Translator | Texas Instruments | TXB0104QPWRQ1
1 | U18 | Voltage Level Translator | Texas Instruments | TXB0106IPWRQ1
8 | U24, U28, U32, U36, U40, U44, U105, U106 | OR Gate (single) | Texas Instruments | SN74LVC1G32DBVT
10 | Q1, Q3, Q4, Q5, Q6, Q7, Q10, Q11, Q12, Q14 | NCh Logic Level Enhancement Mode FET | OnSemi | BSS138K
1 | U5 | ESD Protection Diodes | Diodes Inc. | DRTR5V0U4S-7
2 | U2, U3 | LVTTL/TTL-to-Differential Converter | Analog Devices | MAX9371ESA+
4 | J1, J4, J5, J6 | BNC Ins R/A PCB Skt 50Ohm Black | TE Connectivity | 5227161-6
1 | J17 | JACK 1PORT 1000 BASE-T PCB | TE Connectivity | 6-2301994-2
7 | J13, J14, J18, J19, J20, J21, J30 | SFP+ Connector - see line below for "cage" | Molex | 74441-0010
7 | J13, J14, J18, J19, J20, J21, J30 | Cage for SFP+ connector above | TE Connectivity | 2227023-1 |  |  | Press fit part
1 | U19 | 8-Channel I2C Switch | Texas Instruments | TCA9548APWR
2 | J100, J101 | RF Coaxial Connector U.FL | Hirose Electric | U.FL-R-SMT(10)
1 | L6 | 3.3uH Inductor 8040 case | Wurth Elektronik | 74437358033
Compulsory columns highlighted in yellow

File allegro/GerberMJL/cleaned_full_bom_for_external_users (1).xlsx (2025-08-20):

Description | Qty per BOM | Quantity per batch | Min Quantity to order | Manufacturer | Manufacturer Part Number | Supplier | Supplier Part Number | Designator | Package Type | Technology | Comment | Status | Original Manufacturer Part No from client BOM
CAPACITOR; 0402; 50V; 10%; X7R; -55+125C | 2 | 6 | 6 |  | 0402-10nF-50V | Newbury free stock | 0402-10nF-50V | C1,C3 |  | SMD |  | Newbury free stock | 0402-10nF-50V
CAPACITOR; 0603; 50V; 10%; X7R; -55+125C | 76 | 228 | 228 |  | 0603-100nF-50V | Newbury free stock | 0603-100nF-50V | C5,C6,C8,C11,C53,C54,C56,C58,C59,C60,C62,C64,C69,C71,C72,C74,C75,C78,C79,C83,C84,C86,C115,C116,C117,C119,C123,C132,C133,C135,C136,C138,C155,C156,C158,C159,C161,C178,C179,C181,C182,C184,C201,C202,C204,C205,C207,C224,C225,C227,C228,C230,C247,C248,C250,C251,C253,C270,C271,C2660,C2670,C2690,C2712,C2713,C2714,C2718,C2722,C2723,C2724,C2725,C2726,C2739,C2740,C2741,C2742,C2750 |  | SMD |  | Newbury free stock | 0603-100nF-50V
MURATA - GRM188R61A106KE69D - SMD Multilayer Ceramic Capacitor, 10 µF, 10 V, 0603 [1608 Metric], ± 10%, X5R | 9 | 27 | 4000 | MURATA | GRM188R61A106KE69D | FARNELL | 4540398 | C7,C9,C10,C12,C13,C16,C21,C22,C29 | Cut Tape | SMD |  | Found | GRM188R61A106KE69D
CAPACITOR; 0402; 25V; 10%; X5R; -55+85C | 37 | 111 | 111 |  | 0402-100nF-25V | Newbury free stock | 0402-100nF-25V | C14,C15,C18,C19,C20,C23,C24,C25,C26,C27,C28,C34,C35,C36,C37,C38,C39,C108,C109,C110,C111,C112,C113,C128,C129,C272,C276,C277,C2711,C2735,C2736,C2737,C2738,C3274,C3276,C3716,C3717 |  | SMD |  | Newbury free stock | 0402-100nF-25V
CAPACITOR; 0603; 25V; 10%; X5R; -55+85C | 8 | 24 | 24 |  | 0603-1uF-25V | Newbury free stock | 0603-1uF-25V | C17,C41,C42,C87,C3712,C3713,C3714,C3715 |  | SMD |  | Newbury free stock | 0603-1uF-25V
CAP CER 10UF 25V X5R 0805 | 1 | 3 | 3 | TDK Corporation | C2012X5R1E106K125AB | DIGIKEY | 445-5984-1-ND | C40 | Cut Tape (CT) | SMD |  | Found | C2012X5R1E106K125AB
CAPACITOR; 0603; 25V; 10%; X7R; -55+125C | 2 | 6 | 6 |  | 0603-470nF-25V | Newbury free stock | 0603-470nF-25V | C43,C44 |  | SMD |  | Newbury free stock | 0603-470nF-25V
Multilayer Ceramic Capacitors MLCC - SMD/SMT 963-MSASL21GBB5476MT RPLCMT PN 10V 47uF X5R 0805 20% | 12 | 36 | 36 | TAIYO YUDEN | LMK212BBJ476MG-T | MOUSER | 963-LMK212BBJ476MG-T | C49,C50,C52,C55,C61,C63,C70,C73,C77,C80,C2650,C2680 | Cut Tape | SMD |  | Found | LMK212BBJ476MG-T
CAP CER 5PF 50V NP0 0603 | 1 | 3 | 3 | KYOCERA AVX | 06035A5R0CAT2A | DIGIKEY | 478-12708-1-ND | C51 | Cut Tape (CT) | SMD | obsolete - replaced with alternative | Found | 06035A5R0CAT2A
CAPACITOR; 0603; 50V; 10%; X7R; -55+125C | 5 | 15 | 15 |  | 0603-10nF-50V | Newbury free stock | 0603-10nF-50V | C57,C65,C76,C85,C2710 |  | SMD |  | Newbury free stock | 0603-10nF-50V
CAP CER 100UF 6.3V X5R 1210 | 4 | 12 | 12 | Murata Electronics | GRM32ER60J107ME20L | DIGIKEY | 490-3390-1-ND | C66,C67,C81,C82 | Cut Tape (CT) | SMD |  | Found | GRM32ER60J107ME20L
CAP CER 22UF 25V X5R 1206 | 1 | 3 | 3 | Murata Electronics | GRT31CR61E226ME01L | DIGIKEY | 490-12451-1-ND | C88 | Cut Tape (CT) | SMD |  | Found | GRT31CR61E226ME01L
CAPACITOR; 0805; 50V; 10%; X7R; -55+125C | 4 | 12 | 12 |  | 0805-100nF-50V | Newbury free stock | 0805-100nF-50V | C97,C100,C101,C105 |  | SMD |  | Newbury free stock | 0805-100nF-50V
Multilayer Ceramic Capacitors MLCC - SMD/SMT 1206 25VDC 47uF 20% X5R 1.6mm | 7 | 21 | 21 | TDK | C3216X5R1E476M160AC | MOUSER | 810-C3216X5R1E476M | C98,C99,C102,C103,C104,C106,C107 | Cut Tape | SMD |  | Found | C3216X5R1E476M160AC
CAPACITOR; 0402; 6.3V; 20%; X5R; -55+85C | 1 | 3 | 3 |  | 0402-4.7uF-6.3V | Newbury free stock | 0402-4.7uF-6.3V | C127 |  | SMD |  | Newbury free stock | 0402-4.7uF-6.3V
CAP CER 22UF 25V X5R 0805 | 14 | 42 | 42 | Murata Electronics | GRT21BR61E226ME13L | DIGIKEY | 490-12389-1-ND | C134,C137,C157,C160,C180,C183,C203,C206,C226,C229,C249,C252,C2717,C2719 | Cut Tape (CT) | SMD |  | Found | GRT21BR61E226ME13L
CAPACITOR; 0603; 50V; 5%; C0G/NP0; -55+125C | 18 | 54 | 54 |  | 0603-1nF-50V | Newbury free stock | 0603-1nF-50V | C139,C162,C185,C208,C231,C254,C2727,C2728,C2729,C2730,C2731,C2743,C2744,C2745,C2746,C2747,C2748,C2749 |  | SMD |  | Newbury free stock | 0603-1nF-50V
CAPACITOR; 0603; 10V; 20%; X5R; -55+85C | 2 | 6 | 6 |  | 0603-4.7uF-10V | Newbury free stock | 0603-4.7uF-10V | C274,C275 |  | SMD |  | Newbury free stock | 0603-4.7uF-10V
CAPACITOR; 0402; 10V; 10%; X5R; -55+85C | 1 | 3 | 3 |  | 0402-470nF-10V | Newbury free stock | 0402-470nF-10V | C3718 |  | SMD |  | Newbury free stock | 0402-470nF-10V
LED RED DIFFUSED 0603 SMD | 10 | 30 | 30 | ams-OSRAM USA INC. | LS Q976-NR-1-0-20-R18 | DIGIKEY | 475-LSQ976-NR-1CT-ND | D1,D15,D17,D21,D25,D29,D33,D37,D41,D43 | Cut Tape (CT) | SMD |  | Found | LS Q976-NR-1-0-20-R18
LED GREEN DIFFUSED 0603 SMD | 15 | 45 | 45 | ams-OSRAM USA INC. | LG Q396-PS-35-0-20-R18 | DIGIKEY | 475-LGQ396-PS-35CT-ND | D2,D4,D5,D6,D7,D8,D14,D16,D20,D24,D28,D32,D36,D40,D42 | Cut Tape (CT) | SMD |  | Found | LG Q396-PS-35-0-20-R18
Surface Mount Fuses 32VAC/DC 4A Fast Acting Chip Fuse | 1 | 3 | 3 | Eaton Electronics | TR/3216FF4-R | MOUSER | 504-TR/3216FF4-R | F1 | Cut Tape | SMD |  | Found | TR/3216FF4-R
FUSE BRD MT 750MA 63VAC/VDC 1206 | 1 | 3 | 3 | Bel Fuse Inc. | 0685T0750-01 | DIGIKEY | 5923-0685T0750-01CT-ND | F2 | Cut Tape (CT) | SMD |  | Found | 0685T0750-01
MURATA - DLW5BTM501SQ2L - COMMON MODE FILTER, 500 OHM, 4A | 1 | 3 | 3 | MURATA | DLW5BTM501SQ2L | FARNELL | 3471204 | FL1 | Cut Tape | SMD |  | Found | DLW5BTM501SQ2L
TEXAS INSTRUMENTS - SN74LVC2T45DCUR - Bus Transceiver, LVC Family, 2 Input, 50 mA, 3.9 ns, 1.65 V to 5.5 V, VSSOP-8 | 3 | 9 | 9 | TEXAS INSTRUMENTS | SN74LVC2T45DCUR | FARNELL | 3006798 | IC1,IC2,U47 | Cut Tape | SMD |  | Found | SN74LVC2T45DCUR
AMP - TE CONNECTIVITY - 5227161-6 - RF / Coaxial Connector, BNC Coaxial, Right Angle Jack, Solder, 50 ohm, Phosphor Bronze | 4 | 12 | 12 | AMP - TE CONNECTIVITY | 5227161-6 | FARNELL | 2452496 | J1,J4,J5,J6 | Each | THT | Obsolete - alternative P/N | Found | 5227161-6
Headers & Wire Housings 2.54MM CLASSIC PCB HDR STRIP | 4 | 12 | 12 | Samtec | TSW-102-07-G-S | MOUSER | 200-TSW10207GS | J11,J12,J15,J16 | Standard Pack Qty | THT |  | Found | TSW-102-07-G-S
MOLEX - 74441-0010 - Pluggable I/O Connector, SFP, SFP+, 20 Contacts, 1 x 1 (Single), Surface Mount Right Angle | 7 | 21 | 21 | MOLEX | 74441-0010 | FARNELL | 1463052 | J13,J14,J18,J19,J20,J21,J30 | Cut Tape | THT |  | Found | 74441-0010
TE CONNECTIVITY - 6-2301994-2 - Modular Connector, RJ45 Jack, 1 x 1 (Port), 8P8C, Cat6, Through Hole Mount | 1 | 3 | 3 | TE CONNECTIVITY | 6-2301994-2 | FARNELL | 3791964 | J17 | Each | THT |  | Found | 6-2301994-2
Conn Wire to Board HDR 3 POS 2.54mm Solder ST Top Entry Thru-Hole KK 254 Bag | 3 | 9 | 9 | Molex | 0022232031 | ARROW | 0323_00036981 | J27,J28,J29 | BAG | THT |  | Found | 0022232031
RF Connectors / Coaxial Connectors U.FL RECEPTACLE SMT GLD M CONT REEL | 2 | 6 | 6 | Hirose Connector | U.FL-R-SMT(10) | MOUSER | 798-U.FL-R-SMT10 | J100,J101 | Cut Tape | SMD |  | Found | U.FL-R-SMT10
Connector: pin strips; pin header; male; PIN: 3; straight; THT; 1x3 | 2 | 6 | 6 | SAMTEC | TSW-103-07-G-S | TME | TSW-103-07-G-S | J102,J118 |  | THT |  | Found | TSW-103-07-G-S
Conn Wire to Board HDR 4 POS 4.2mm Solder RA Side Entry Thru-Hole Mini-Fit Jr Tray | 1 | 3 | 3 | Molex | 1724480004 | ARROW | 0323_08349238 | J300 | PACK | THT |  | Found | 1724480004
Board to Board & Mezzanine Connectors ASP | 1 | 3 | 3 | Samtec | ASP-134606-01 | MOUSER | 200-ASP-134606-01 | J8 | Cut Tape | SMD |  | Found | ASP-134606-01
FERRITE BEAD 120 OHM 0805 1LN | 6 | 18 | 18 | Laird-Signal Integrity Products | LI0805H121R-10 | DIGIKEY | 240-2383-1-ND | L1,L2,L3,L5,L19,L22 | Cut Tape (CT) | SMD |  | Found | LI0805H121R-10
WURTH ELEKTRONIK - 74437358033 - Power Inductor (SMD), 3.3 µH, 8.25 A, Shielded, 20 A, WE-LHMI Series | 1 | 3 | 3 | WURTH ELEKTRONIK | 74437358033 | FARNELL | 3237507 | L6 | Cut Tape | SMD |  | Found | 74437358033
MURATA - LQH32CN4R7M23L - Power Inductor (SMD), 4.7 µH, 450 mA, Unshielded, LQH32CN_23 Series, 1210 [3225 Metric] | 14 | 42 | 42 | MURATA | LQH32CN4R7M23L | FARNELL | 3471296 | L7,L8,L9,L10,L11,L12,L13,L14,L15,L16,L17,L18,L20,L21 | Cut Tape | SMD |  | Found | LQH32CN4R7M23L
MOSFET N-CH 50V 220MA SOT23-3 | 10 | 30 | 30 | onsemi | BSS138K | DIGIKEY | BSS138KCT-ND | Q1,Q3,Q4,Q5,Q6,Q7,Q10,Q11,Q12,Q14 | Cut Tape (CT) | SMD |  | Found | BSS138K
RESISTOR; 0402; 0.0625W; 100ppm; 1%; 50V; -55+125C | 20 | 60 | 60 |  | 0402-1K | Newbury free stock | 0402-1K | R1,R10,R19,R20,R21,R22,R23,R24,R25,R26,R81,R82,R106,R107,R110,R111,R254,R2670,R2694,R3270 |  | SMD |  | Newbury free stock | 0402-1K
RES SMD 24.9 OHM 1% 1/10W 0603 | 2 | 6 | 6 | Panasonic Electronic Components | ERJ-3EKF24R9V | DIGIKEY | P24.9HCT-ND | R2,R4 | Cut Tape (CT) | SMD |  | Found | ERJ-3EKF24R9V
RESISTOR; 0603; 0.1W; 400ppm; ≤50mΩ; 75V; -55+125C | 5 | 15 | 15 |  | 0603-0R | Newbury free stock | 0603-0R | R9,R71,R72,R73,R253 |  | SMD |  | Newbury free stock | 0603-0R
RES SMD 133 OHM 1% 1/10W 0603 | 4 | 12 | 12 | Panasonic Electronic Components | ERJ-3EKF1330V | DIGIKEY | P133HCT-ND | R11,R12,R15,R16 | Cut Tape (CT) | SMD |  | Found | ERJ-3EKF1330V
RESISTOR; 0603; 0.1W; 100ppm; 1%; 75V; -55+125C | 4 | 12 | 12 |  | 0603-68R | Newbury free stock | 0603-68R | R13,R14,R17,R18 |  | SMD |  | Newbury free stock | 0603-68R
RESISTOR; 0402; 0.0625W; 100ppm; 1%; 50V; -55+125C | 5 | 15 | 15 |  | 0402-100R | Newbury free stock | 0402-100R | R31,R35,R1540,R2692,R2693 |  | SMD |  | Newbury free stock | 0402-100R
RESISTOR; 0402; 0.0625W; 200ppm; 1%; 50V; -55+125C | 2 | 6 | 6 |  | 0402-75R | Newbury free stock | 0402-75R | R32,R34 |  | SMD |  | Newbury free stock | 0402-75R
RESISTOR; 0603; 0.1W; 100ppm; 1%; 75V; -55+125C | 1 | 3 | 3 |  | 0603-1K | Newbury free stock | 0603-1K | R33 |  | SMD |  | Newbury free stock | 0603-1K
RESISTOR; 0603; 0.1W; 100ppm; 1%; 75V; -55+125C | 1 | 3 | 3 |  | 0603-390K | Newbury free stock | 0603-390K | R36 |  | SMD |  | Newbury free stock | 0603-390K
RESISTOR; 0805; 0.125W; 100ppm; 1%; 150V; -55+125C | 9 | 27 | 27 |  | 0805-75R | Newbury free stock | 0805-75R | R37,R39,R43,R44,R51,R57,R62,R74,R80 |  | SMD |  | Newbury free stock | 0805-75R
RES 4.99K OHM 1% 1/10W 0603 | 18 | 54 | 54 | Stackpole Electronics Inc | RMCF0603FT4K99 | DIGIKEY | RMCF0603FT4K99CT-ND | R38,R40,R50,R56,R61,R2660,R128,R130,R149,R151,R170,R172,R191,R193,R212,R214,R233,R235 | Cut Tape (CT) | SMD |  | Found | RMCF0603FT4K99
RESISTOR; 0603; 0.1W; 100ppm; 1%; 75V; -55+125C | 1 | 3 | 3 |  | 0603-1M | Newbury free stock | 0603-1M | R41 |  | SMD |  | Newbury free stock | 0603-1M
RES SMD 17.8K OHM 1% 1/10W 0603 | 1 | 3 | 3 | Panasonic Electronic Components | ERJ-3EKF1782V | DIGIKEY | P17.8KHCT-ND | R42 | Cut Tape (CT) | SMD |  | Found | ERJ-3EKF1782V
RES 12.1K OHM 1% 1/10W 0603 | 1 | 3 | 3 | Stackpole Electronics Inc | RMCF0603FT12K1 | DIGIKEY | RMCF0603FT12K1CT-ND | R46 | Cut Tape (CT) | SMD |  | Found | RMCF0603FT12K1
RES 2.32K OHM 1% 1/10W 0603 | 1 | 3 | 3 | Stackpole Electronics Inc | RMCF0603FT2K32 | DIGIKEY | RMCF0603FT2K32CT-ND | R47 | Cut Tape (CT) | SMD |  | Found | RMCF0603FT2K32
RESISTOR; 0402; 0.0625W; 400ppm; ≤50mΩ; 50V; -55+125C | 35 | 105 | 105 |  | 0402-0R | Newbury free stock | 0402-0R | R48,R49,R59,R60,R63,R64,R65,R70,R112,R113,R114,R115,R118,R247,R248,R249,R250,R255,R256,R257,R258,R259,R260,R261,R262,R263,R2661,R2662,R2663,R2664,R2665,R2666,R3696,R3697,R265 |  | SMD |  | Newbury free stock | 0402-0R
RES 0.02 OHM 1% 1/4W 0805 | 7 | 21 | 21 | Stackpole Electronics Inc | CSR0805FK20L0 | DIGIKEY | CSR0805FK20L0CT-ND | R52,R54,R2667,R2668,R53,R58,R2671 | Cut Tape (CT) | SMD | Not available & P/N is wrong. Use 0.02R as a temp bodge | Found | CSR0805FK20L0
RES SMD 97.6K OHM 1% 1/10W 0402 | 1 | 3 | 3 | Panasonic Electronic Components | ERJ-2RKF9762X | DIGIKEY | P97.6KLCT-ND | R78 | Cut Tape (CT) | SMD |  | Found | ERJ-2RKF9762X
RESISTOR; 0402; 0.0625W; 100ppm; 1%; 50V; -55+125C | 1 | 3 | 3 |  | 0402-20K | Newbury free stock | 0402-20K | R79 |  | SMD |  | Newbury free stock | 0402-20K
RESISTOR; 0603; 0.1W; 100ppm; 1%; 75V; -55+125C | 22 | 66 | 66 |  | 0603-4K7 | Newbury free stock | 0603-4K7 | R83,R84,R85,R86,R87,R88,R89,R90,R91,R92,R96,R97,R98,R99,R100,R101,R102,R103,R245,R246,R251,R252 |  | SMD |  | Newbury free stock | 0603-4K7
PANASONIC - ERJ2RKF4991X - SMD Chip Resistor, 4.99 kohm, ± 1%, 100 mW, 0402 [1005 Metric], Thick Film, Precision | 3 | 9 | 10 | PANASONIC | ERJ2RKF4991X | FARNELL | 2059145 | R93,R94,R95 | Cut Tape | SMD |  | Found | ERJ2RKF4991X
Thin Film Resistors - SMD 0603 49.9ohm 0.1% 25ppm | 16 | 48 | 48 | Panasonic | ERA-3AEB49R9V | MOUSER | 667-ERA-3AEB49R9V | R104,R105,R108,R109,R119,R120,R140,R141,R161,R162,R182,R183,R203,R204,R224,R225 | Cut Tape | SMD | Thin film for high freq use | Found | ERA-3AEB49R9V
RESISTOR; 0603; 0.1W; 100ppm; 1%; 75V; -55+125C | 1 | 3 | 3 |  | 0603-100R | Newbury free stock | 0603-100R | R116 |  | SMD |  | Newbury free stock | 0603-100R
RESISTOR; 0603; 0.1W; 100ppm; 1%; 75V; -55+125C | 17 | 51 | 51 |  | 0603-200R | Newbury free stock | 0603-200R | R117,R132,R133,R153,R154,R174,R175,R195,R196,R216,R217,R237,R238,R2684,R2685,R2690,R2691 |  | SMD |  | Newbury free stock | 0603-200R
RESISTOR; 0402; 0.0625W; 100ppm; 1%; 50V; -55+125C | 30 | 90 | 90 |  | 0402-4K7 | Newbury free stock | 0402-4K7 | R124,R125,R127,R129,R145,R146,R148,R150,R166,R167,R169,R171,R187,R188,R190,R192,R208,R209,R211,R213,R229,R230,R232,R234,R2676,R2677,R2679,R2681,R2696,R3698 |  | SMD |  | Newbury free stock | 0402-4K7
RES 143K OHM 1% 1/10W 0603 | 1 | 3 | 3 | Stackpole Electronics Inc | RMCF0603FT143K | DIGIKEY | RMCF0603FT143KCT-ND | R2640 | Cut Tape (CT) | SMD |  | Found | RMCF0603FT143K
RES SMD 280K OHM 1% 1/16W 0402 | 1 | 3 | 3 | Bourns Inc. | CR0402-FX-2803GLF | DIGIKEY | CR0402-FX-2803GLFCT-ND | R2650 | Cut Tape (CT) | SMD |  | Found | CR0402-FX-2803GLF
LTC6957IDD-2#PBF | 1 | 3 | 3 |  | LTC6957IDD-2#PBF | Client |  | U1 |  | SMD | obsolete? Seems various chip-brokers have stock though. | I'll supply | LTC6957IDD-2#PBF
ANALOG DEVICES - MAX9371ESA+ - Translator, LVTTL/TTL-to-Differential LVPECL/PECL, 1 Input, 50 mA, 270 ps, 3 V to 5.25 V, NSOIC-8 | 2 | 6 | 6 | ANALOG DEVICES | MAX9371ESA+ | FARNELL | 2516400 | U2,U3 | Each | SMD | Avoid Digikey - £100 special shipping | Found | MAX9371ESA+
TVS DIODE 5.5VWM SOT363 | 1 | 3 | 3 | Diodes Incorporated | DRTR5V0U4S-7 | DIGIKEY | DRTR5V0U4S-7DICT-ND | U5 | Cut Tape (CT) | SMD |  | Found | DRTR5V0U4S-7
ANALOG DEVICES - LT8645SJV-2#PBF - DC-DC Switching Synchronous Buck Regulator, Adjustable, 3.4V to 64V in, LQFN-EP-32 | 1 | 3 | 3 | ANALOG DEVICES | LT8645SJV-2#PBF | FARNELL | 4407063 | U6 | Each | SMD |  | Found | LT8645SJV-2#PBF
LDO Voltage Regulators High-Current (4 A) L DO Volt Regulator A 595-TPS7A8500RGRR | 5 | 15 | 15 | Texas Instruments | TPS7A8500RGRT | MOUSER | 595-TPS7A8500RGRT | U7,U9,U11,U12,U101 | Cut Tape | SMD |  | Found | TPS7A8500RGRT
ANALOG DEVICES - LTC2945CUD#PBF - Power Monitor, 2.7 V to 80 V in, QFN-EP, 12-Pins, 0 °C to 70 °C | 3 | 9 | 9 | ANALOG DEVICES | LTC2945CUD#PBF | FARNELL | 4028343 | U8,U10,U13 | Each | SMD |  | Found | LTC2945CUD#PBF
IC SUPERVISOR 1 CHANNEL 6SON | 1 | 3 | 3 | Texas Instruments | TPS3895ADRYR | DIGIKEY | 296-29806-1-ND | U15 | Cut Tape (CT) | SMD |  | Found | TPS3895ADRYR
IC XLTR VL BIDIR 14-TSSOP | 1 | 3 | 3 | Texas Instruments | TXB0104QPWRQ1 | DIGIKEY | 296-27760-1-ND | U17 | Cut Tape (CT) | SMD |  | Found | TXB0104QPWRQ1
IC XLTR VL BIDIR 16-TSSOP | 2 | 6 | 6 | Texas Instruments | TXB0106IPWRQ1 | DIGIKEY | 296-24960-1-ND | U18,U347 | Cut Tape (CT) | SMD |  | Found | TXB0106IPWRQ1
TEXAS INSTRUMENTS - TCA9548APWR - Specialized Interface, I2C, SMBus, Servers & Routers, 1.65 V, 5.5 V, TSSOP, 24 Pins | 1 | 3 | 3 | TEXAS INSTRUMENTS | TCA9548APWR | FARNELL | 3124884 | U19 | Cut Tape | SMD |  | Found | TCA9548APWR
IC FF D-TYPE SINGLE 1BIT 16QFN | 6 | 18 | 18 | onsemi | NB7V52MMNG | DIGIKEY | NB7V52MMNGOS-ND | U22,U26,U30,U34,U38,U42 | Tube | SMD |  | Found | NB7V52MMNG
Board Mount Temperature Sensors Digital Temp Sensor & Thermal Watchdog A 926-LM75AIM/NOPB | 1 | 3 | 3 | Texas Instruments | LM75AIMX/NOPB | MOUSER | 926-LM75AIMX/NOPB | U46 | Cut Tape | SMD |  | Found | LM75AIMX/NOPB
Clock Generator 0.008MHz to 750MHz-IN 1028MHz-OUT 64-Pin QFN EP | 1 | 3 | 3 | Skyworks Solutions | SI5395A-A-GM | ARROW | 1762_12545901 | U48 | TRAY | SMD |  | Found | SI5395A-A-GM
EEPROM 2K 256 X 8 1.8V SERIAL EE, IND | 1 | 3 | 3 | Microchip Technology | 24AA025E48T-I/SN | MOUSER | 579-24AA025E48T-I/SN | U49 | Cut Tape | SMD |  | Found | 24AA025E48T-I/SN
IC XPND 400KHZ I2C SMBUS 24TSSOP | 2 | 6 | 6 | Texas Instruments | TCA9539PWR | DIGIKEY | 296-25130-1-ND | U52,U53 | Cut Tape (CT) | SMD |  | Found | TCA9539PWR
ANALOG DEVICES - LTM8029IY#PBF - DC/DC POL Converter, Adjustable, Buck, 4.5 to 36 V in, 1.2 to 18V/0.6A out, BGA-35 | 1 | 3 | 3 | ANALOG DEVICES | LTM8029IY#PBF | FARNELL | 4029530 | U100 | Each | SMD |  | Found | LTM8029IY#PBF
IC REG LINEAR 1.8V 1A 8-SON | 1 | 3 | 3 | Texas Instruments | TPS74618PQWDRBRQ1 | DIGIKEY | 296-TPS74618PQWDRBRQ1CT-ND | U102 | Cut Tape (CT) | SMD |  | Found | TPS74618PQWDRBRQ1
Encoders, Decoders, Multiplexers & Demultiplexers 4.25Gbps 2:1 LVPECL Multiplexer w/ FSI Inputs | 1 | 3 | 3 | Microchip Technology | SY58608UMG | MOUSER | 998-SY58608UMG | U107 | Standard Pack Qty | SMD |  | Found | SY58608UMG
IC CLOCK/DATA RECOVERY 32-LFCSP | 1 | 3 | 3 | Analog Devices Inc. | ADN2818ACPZ | DIGIKEY | ADN2818ACPZ-ND | U110 | Tray | SMD | Hard to get hold of! BoM calls for ADN2817..., fit lower spec ADN2818 instead. | Found | ADN2818ACPZ
IC INVERTER 2CH 2-INP SOT26 | 8 | 24 | 24 | Diodes Incorporated | 74LVC2G04W6-7 | DIGIKEY | 74LVC2G04W6-7DICT-ND | U348,U349,U350,U351,U352,U353,U354,U355 | Cut Tape (CT) | SMD |  | Found | 74LVC2G04W6-7
MEMS OSC TCXO 50.0000MHZ LVDS | 2 | 6 | 6 | SiTime | SIT5021AI-2DE-25E-50.000000X | DIGIKEY | 1473-30178-1-ND | Y1,Y2 | Cut Tape (CT) | SMD |  | Found | SIT5021AI-2DE-25E-50.000000X

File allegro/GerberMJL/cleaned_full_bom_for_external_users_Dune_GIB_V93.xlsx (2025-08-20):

W/Days | 3 Qty | Price breakdown
9 | - |  | Each | Batch | W/Days
10 | - | PCB | £ 617.31 | £ 1851.93 | 5 W/Days
15 | £ 5051.38 | Assembly | £ 619.79 | £ 1859.38 | 10 W/Days
20 | £ 4613.41 | Components | £ 446.69 | £ 1340.07 | 0 W/Days
25 | £ 4445.29 | TOTAL | £ 1683.79 | £ 5051.38 | 15 W/Days
30 | £ 4226.29
45 | £ 3974.11

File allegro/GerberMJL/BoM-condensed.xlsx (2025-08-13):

Item Number | Quantity | Value | Description | Part Number | Part Reference | Manufacturer Part Number | Manufacturer | Distributor Part Number | Distributor | Voltage | Tolerance
1 | 2 | 0.01UF |  | C0402C103K3RACTU | C1,C3 |  |  |  |  | 25V | 10%
2 | 76 | 0.1UF |  | 445-1316-2-ND | C5,C6,C8,C11,C53,C54,C56,C58,C59,C60,C62,C64,C69,C71,C72,C74,C75,C78,C79,C83,C84,C86,C115,C116,C117,C119,C123,C132,C133,C135,C136,C138,C155,C156,C158,C159,C161,C178,C179,C181,C182,C184,C201,C202,C204,C205,C207,C224,C225,C227,C228,C230,C247,C248,C250,C251,C253,C270,C271,C2660,C2670,C2690,C2712,C2713,C2714,C2718,C2722,C2723,C2724,C2725,C2726,C2739,C2740,C2741,C2742,C2750 |  |  |  |  | 25V
3 | 9 | 10UF |  | GRM188R61A106KE69D | C7,C9,C10,C12,C13,C16,C21,C22,C29 |  |  |  |  | 10V | 10%
4 | 37 | 0.1UF |  | 445-7348-2-ND | C14,C15,C18,C19,C20,C23,C24,C25,C26,C27,C28,C34,C35,C36,C37,C38,C39,C108,C109,C110,C111,C112,C113,C128,C129,C272,C276,C277,C2711,C2735,C2736,C2737,C2738,C3274,C3276,C3716,C3717 |  |  |  |  | 25V
5 | 8 | 1UF |  | C1608X7R1E105M080AB | C17,C41,C42,C87,C3712,C3713,C3714,C3715 |  |  |  |  | 25V
6 | 1 | 10UF |  | 445-5984-1-ND | C40 |  |  |  |  | 25V
7 | 2 | 0.47UF |  | CC0603KRX5R8BB474 | C43,C44 |  |  |  |  | 25V | 10%
8 | 12 | 47UF |  | 587-5465-6-ND | C49,C50,C52,C55,C61,C63,C70,C73,C77,C80,C2650,C2680 |  |  |  |  | 10V
9 | 1 | 5.0PF | CAP 5.0PF 50V CERAMIC 0603 SMD | PCC050CVTR-ND | C51 | ECU-V1H050CCV | Panasonic - SCD | PCC050CVTR-ND | Digi-Key | 50V
10 | 5 | 0.01UF |  | C0603C103F3GACTU | C57,C65,C76,C85,C2710 |  |  |  |  | 25V
11 | 4 | 100UF |  | GRM32ER60J107ME20L | C66,C67,C81,C82 |  |  |  |  | 6.3V | 20%
12 | 1 | 22UF |  | GRT31CR61E226ME01L | C88 |  |  |  |  | 25V | 20%
13 | 4 | 0.1UF |  | 445-8173-1-ND | C97,C100,C101,C105 |  |  |  |  | 25V
14 | 7 | 47UF |  | C3216X5R1E476M160AC | C98,C99,C102,C103,C104,C106,C107 |  |  |  |  | 25V | 20%
15 | 1 | 4.7UF |  | GRM155R60J475ME87D | C127 |  |  |  |  | 6.3V
16 | 14 | 22UF |  | GRT21BR61E226ME13L | C134,C137,C157,C160,C180,C183,C203,C206,C226,C229,C249,C252,C2717,C2719 |  |  |  |  | 25V | 20%
17 | 18 | 1000PF | CAP 1000PF 50V CERAMIC 0603 SMD | PCC102BVTR-ND | C139,C162,C185,C208,C231,C254,C2727,C2728,C2729,C2730,C2731,C2743,C2744,C2745,C2746,C2747,C2748,C2749 | ECU-V1H102KBV | Panasonic - SCD | PCC102BVTR-ND | Digi-Key | 50V
18 | 2 | 4.7UF |  | C0603C475M8PACTU | C274,C275 |  |  |  |  | 10V | 20%
19 | 1 | 0.47UF |  | GRM155R60J474KE19J | C3718 |  |  |  |  | 6.3V
20 | 1 | RED |  | LS L296-P2Q2-1-Z | D1
21 | 15 | GREEN |  | LG Q396-PS-35 | D2,D4,D5,D6,D7,D8,D14,D16,D20,D24,D28,D32,D36,D40,D42
22 | 9 | RED |  | LS Q976-NR-1 | D15,D17,D21,D25,D29,D33,D37,D41,D43
23 | 1 | 4A |  | TR/3216FF4-R | F1
24 | 1 | 0.75A |  | 0685T0750-01 | F2
25 | 1 | 120 Ohm@100MHz |  | DLW5BTM501SQ2L | FL1
26 | 3 | SN74LVC2T45DCU |  | SN74LVC2T45DCU | IC1,IC2,U47
27 | 4 | BNC/R |  | 1-1634612-0 | J1,J4,J5,J6
28 | 4 | HDR1x2 |  | HDR1x2 | J11,J12,J15,J16
29 | 7 | 0744410010 |  | 0744410010 | J13,J14,J18,J19,J20,J21,J30
30 | 1 | 6-2301994-2 |  | 6-2301994-2 | J17
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

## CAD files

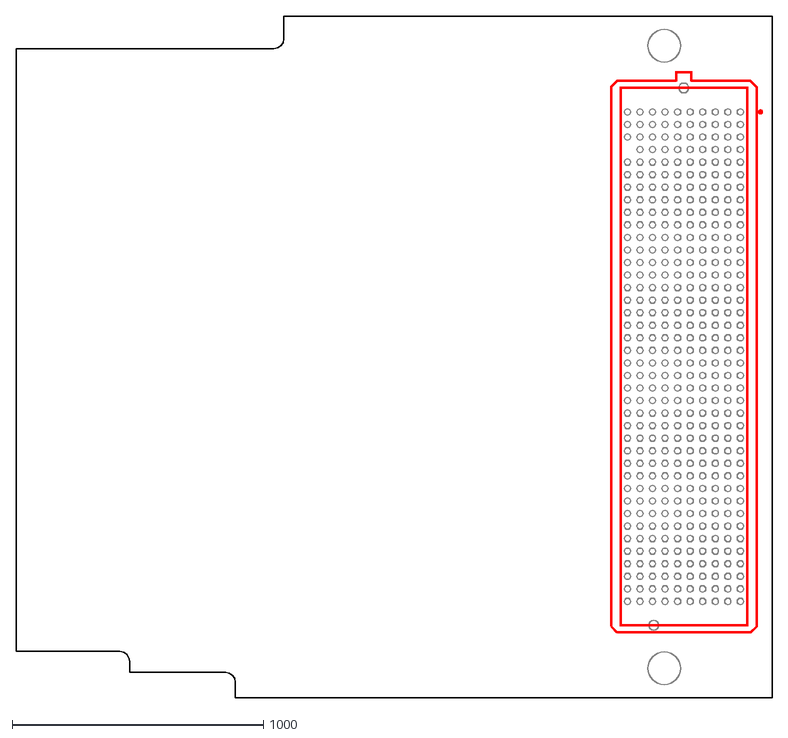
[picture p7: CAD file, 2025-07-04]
allegro/dune_outline.dxf
3011.8 x 2716.5

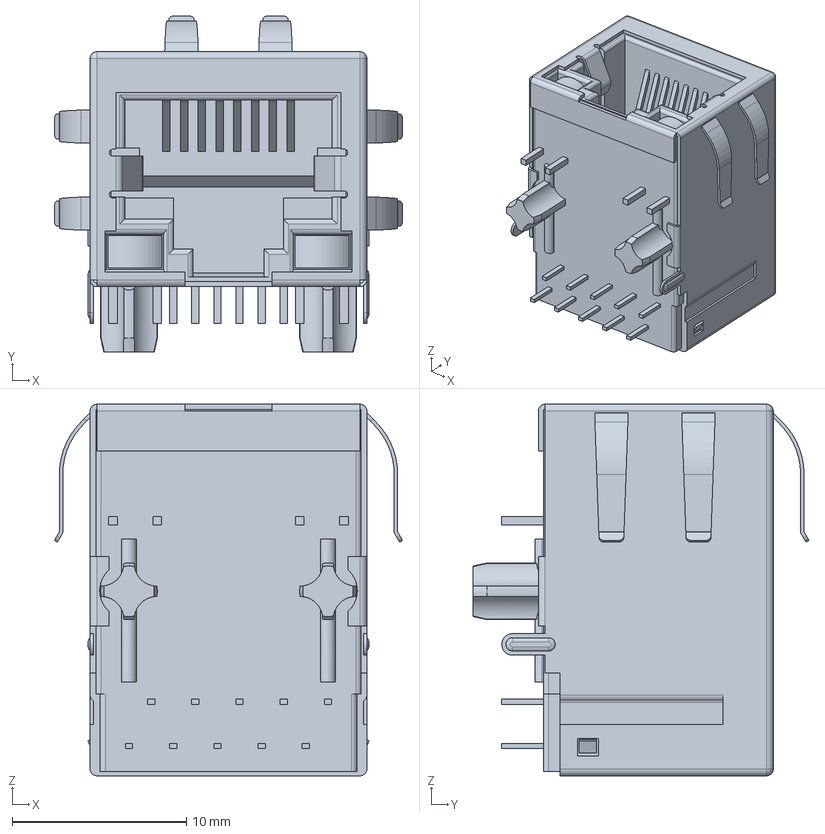
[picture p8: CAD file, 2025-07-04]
allegro/exp_sym/6-2301994-2.stp
20.0 x 19.3 x 21.4 mm

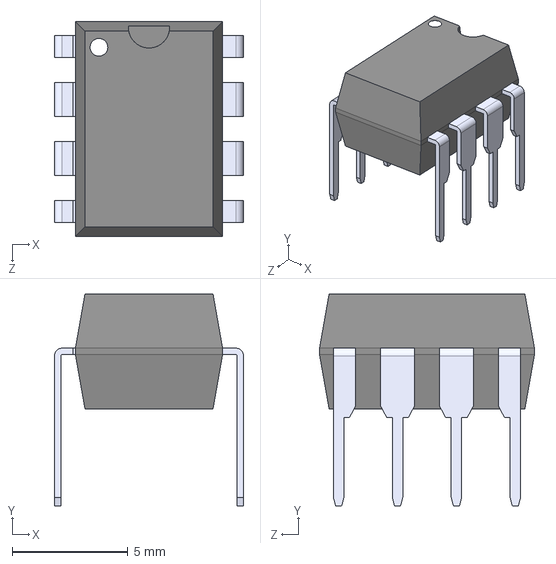
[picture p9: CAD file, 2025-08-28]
PCB_Health/LT1025CN8_PBF/LT1025CN8_PBF.step
8.15 x 9.14 x 9.27 mm

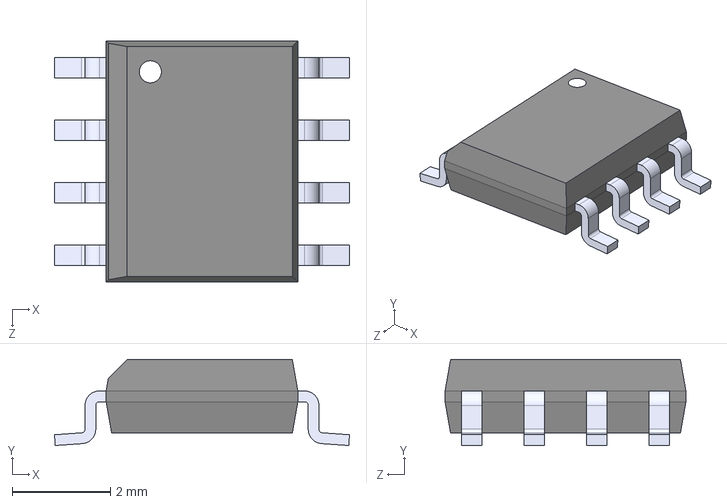
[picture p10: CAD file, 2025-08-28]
PCB_Health/MAX6675ISA_/MAX6675ISA_.step
6.00 x 1.75 x 4.90 mm

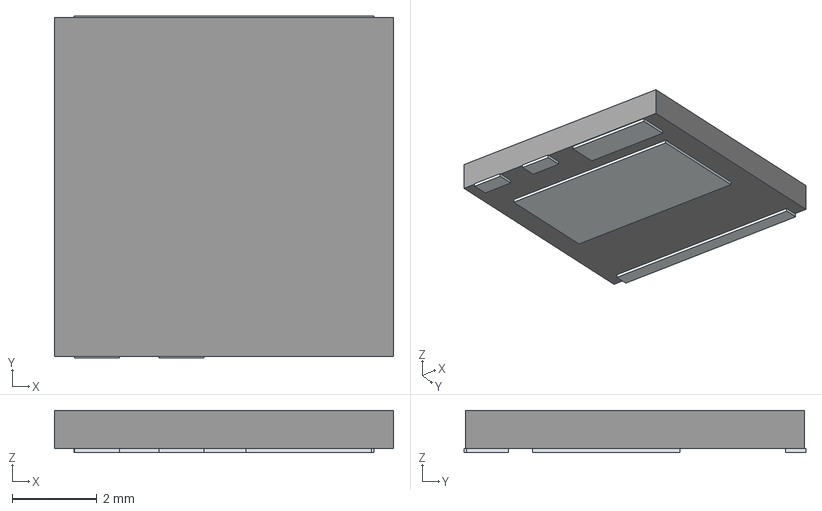
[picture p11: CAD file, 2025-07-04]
allegro/exp_sym/allegro/GNP1150TCA-ZE2.stp
8.00 x 8.07 x 1.00 mm
Pins

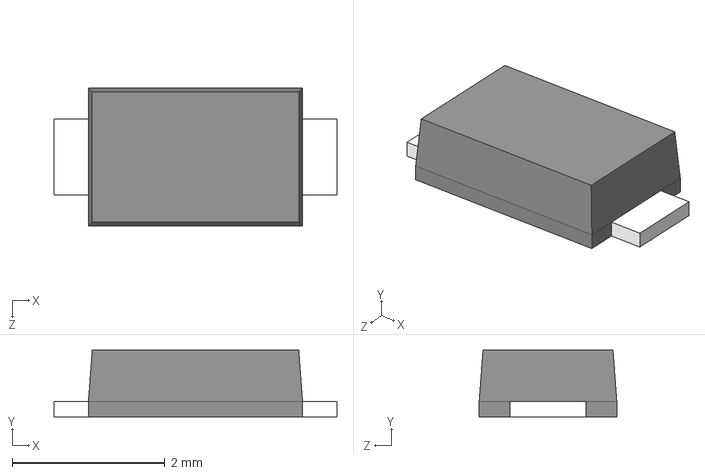
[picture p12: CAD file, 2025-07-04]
allegro/exp_sym/allegro/SS16FP.stp
3.70 x 0.875 x 1.80 mm

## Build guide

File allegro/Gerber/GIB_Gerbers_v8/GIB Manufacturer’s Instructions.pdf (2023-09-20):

GIB Manufacturer’s Instructions

University of Pennsylvania – Dept. Physics BOARD NAME: GPS Interface Board

DATE: July 2020
CONTACTS:
Jon Sensenig: jonsensenig17@gmail.com 717-468-1292
Rick Van Berg rick@hep.upenn.edu
(215) 898-5977

MANUFACTURING NOTES

1. This is an 8 layer board Layer order:
1. TOP
2. GND1
3. SIG
4 GND2
5. PWR1
6. PWR2
7. GND3
8. BOTTOM
2. MATERIAL: FR4
3. BOARD THICKNESS: Approx. 0.060 inches – non-critical.
4. COPPER THICKNESSES: ½ oz or best practice.
5. All holes are plated through unless otherwise noted.
6. Smallest hole size 10mils.
7. GOLD FINISH
8. NOTE: To clarify any possible ambiguity in the Gerber files, the 2 slots at board locations (x,y) = (299mils, 5384mils) and (981mils, 5384mils) are rectangular through-hole plated slots. The width of the slot should be x = 90mils and y = 130mils.

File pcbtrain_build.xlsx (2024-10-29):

mm | thousandth | rnd
0.025 | 0.9842519685 | 1.0 | 2.55 | mm
0.035 | 1.377952756 | 1.4 | 100.3937008 | thou
0.11 | 4.330708661 | 4.3 | 100.4 | thou
0.11 | 4.330708661 | 4.3
0.11 | 4.330708661 | 4.3
0.035 | 1.377952756 | 1.4
0.3 | 11.81102362 | 11.8
0.035 | 1.377952756 | 1.4
0.11 | 4.330708661 | 4.3
0.11 | 4.330708661 | 4.3
0.11 | 4.330708661 | 4.3
0.035 | 1.377952756 | 1.4
0.3 | 11.81102362 | 11.8
0.035 | 1.377952756 | 1.4
0.11 | 4.330708661 | 4.3
0.11 | 4.330708661 | 4.3
0.11 | 4.330708661 | 4.3
0.035 | 1.377952756 | 1.4
0.3 | 11.81102362 | 11.8
0.035 | 1.377952756 | 1.4
0.11 | 4.330708661 | 4.3
0.11 | 4.330708661 | 4.3
0.11 | 4.330708661 | 4.3
0.035 | 1.377952756 | 1.4
0.025 | 0.9842519685 | 1.0

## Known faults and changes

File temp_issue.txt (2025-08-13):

SFPs are defined as a single component symbol.

Symbol gives a TE part number on hover-over text (TE_2227023) which is an SFP cage only.

Symbol has Device Type defined as "CON20P_SFP-1367073-1_TE_2227023" which is a mash-up of a Molex part number for electrical connector and TE part number for cage.

Symbol has footprint of te_2227023-1.psm which seems to include electrical pads which aren't really part of TE_2227023 which is just a cage.

Symbol has a Value defined as 0744410010 which is a part number for a Molex SFP electrical connector

This all means that somehow the Molex electrical connector has propagated through to to BoM, but no cages are on the BoM. Even though the symbol gives the cage part number in Allegro (but no electrical connector)

Centroid for symbol appears to be centroid of electrical pads. So that probably woks fine for P&Ping the connector but not the cage.

Probably wants redoing as two separate symbols which can be placed on PCB and locked together. Then parts and P&P info will cascade through to BoM and P&P file properly.

Is it necessary/sensible to have two different manufacturer's parts like this? Can we get both parts from TE or Molex?

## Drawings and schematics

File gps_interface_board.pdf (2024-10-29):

## Part I2C Address

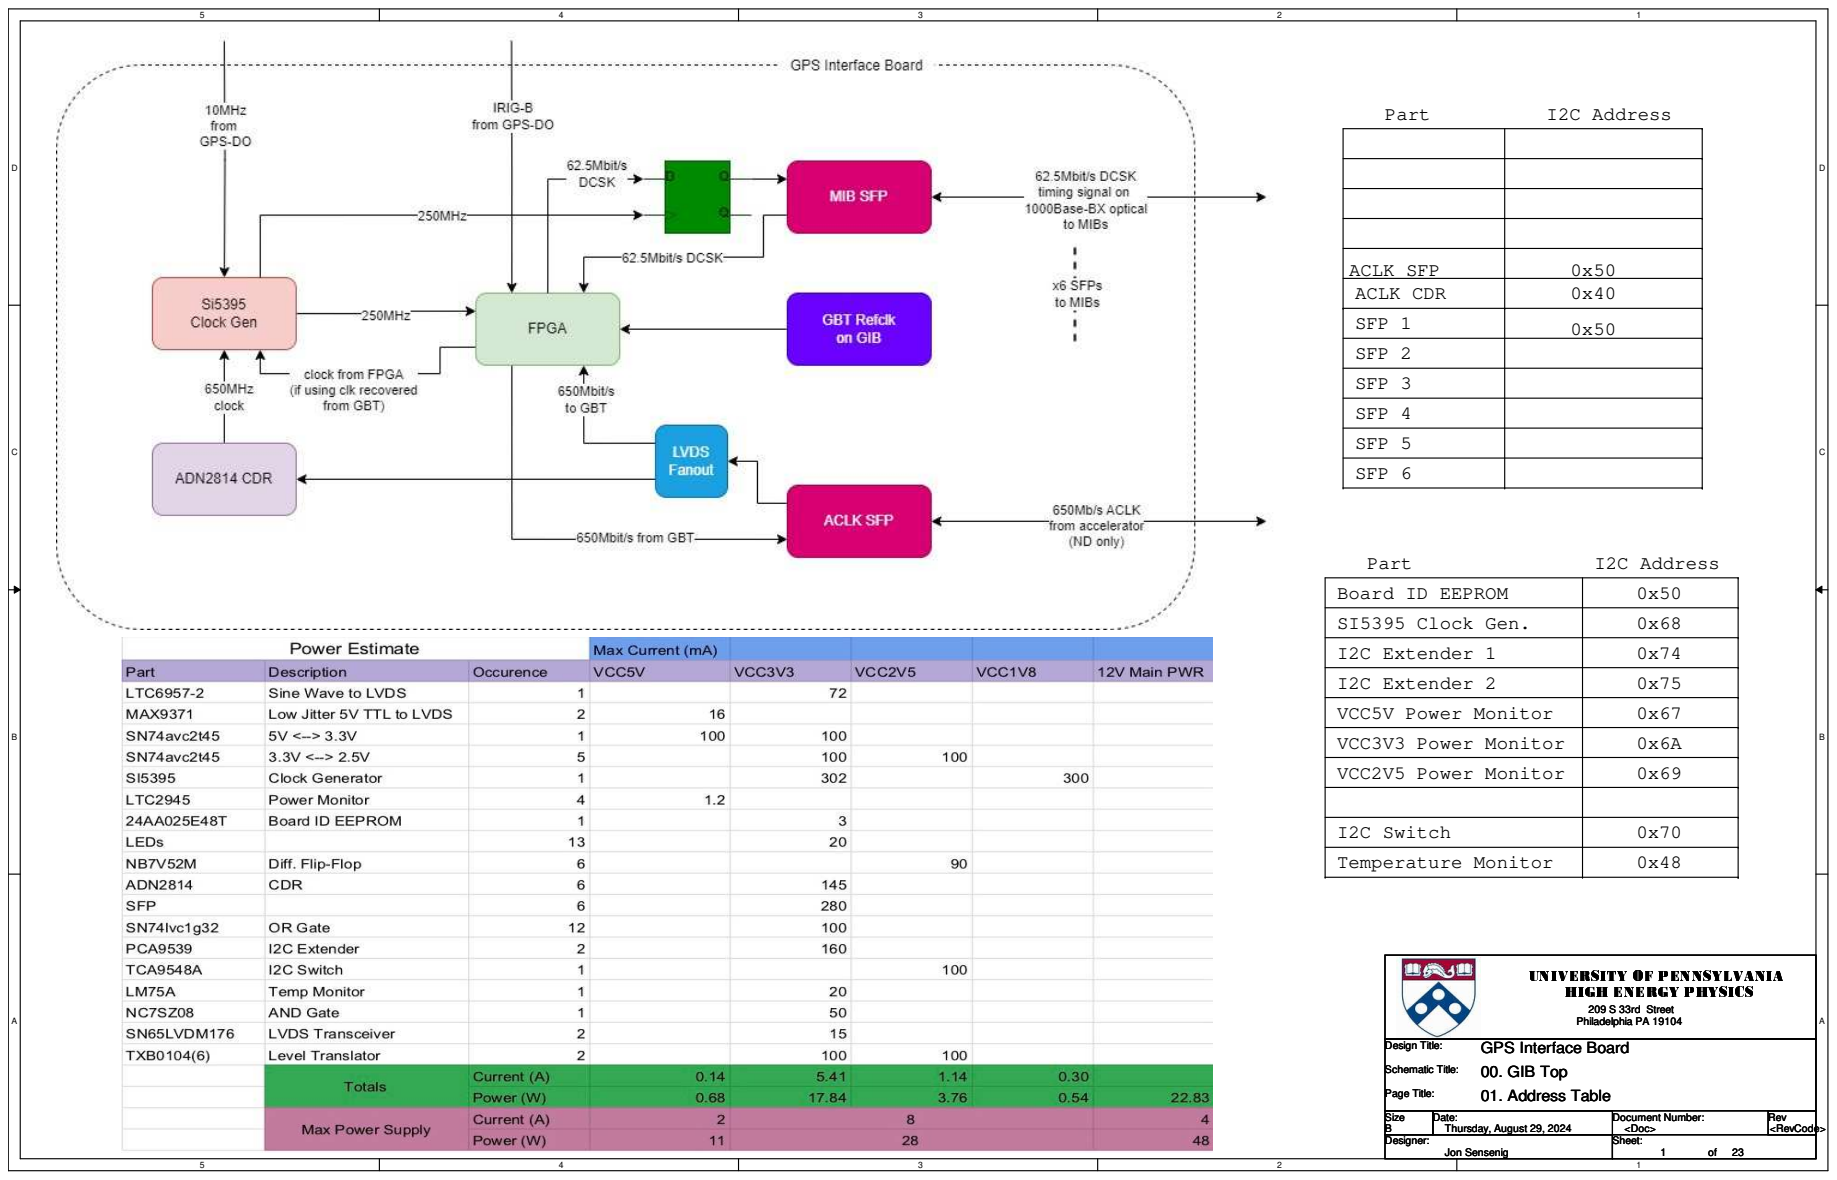
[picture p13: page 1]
SFP 1; I2C AddressPart; Size; Document Number:; RevDate:; Sheet:; Designer:; Design Title:; 209 S 33rd Street Philadelphia PA 19104; Schematic Title:; Page Title:; <Doc>; <RevCode>B; Thursday, August 29, 2024; Jon Sensenig

ACLK SFP | 0x50
0x40ACLK CDR

SFP 2

SFP 3

SFP 4

SFP 5

SFP 6

Board ID EEPROM | 0x50

SI5395 Clock Gen. | 0x68

I2C Extender 1 | 0x74

I2C Extender 2 | 0x75

VCC5V Power Monitor | 0x67

VCC3V3 Power Monitor | 0x6A

VCC2V5 Power Monitor | 0x69

I2C Switch | 0x70

Temperature Monitor | 0x48

GPS Interface Board
00. GIB Top
01. Address Table

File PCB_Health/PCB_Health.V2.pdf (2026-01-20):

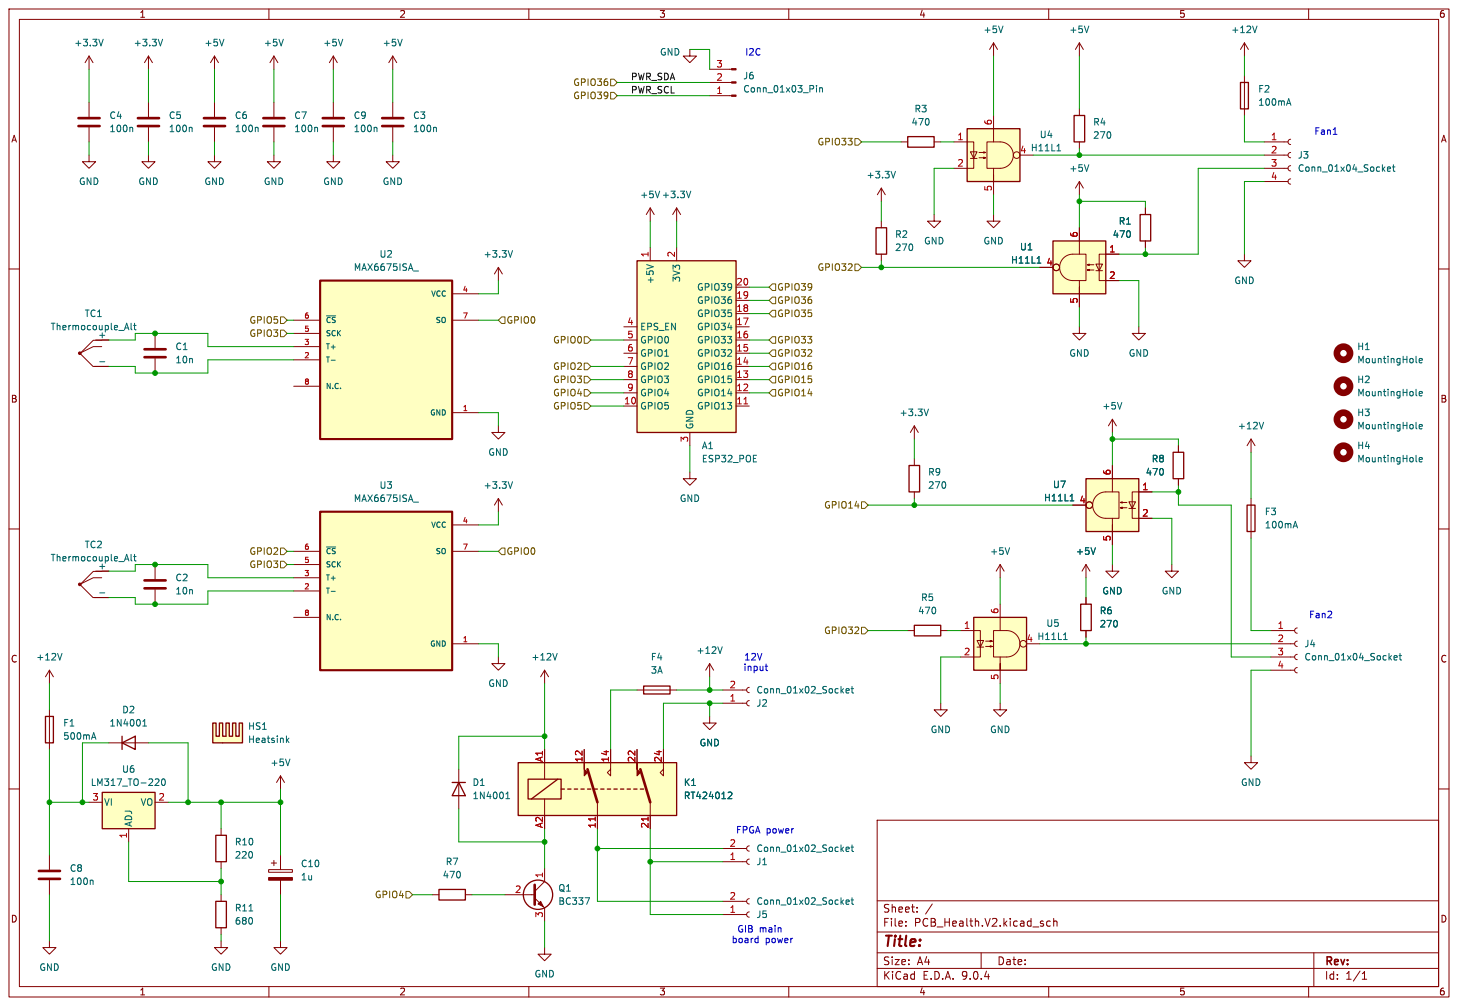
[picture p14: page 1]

Id: 1/1 Title: File: PCB_Health.V2.kicad_sch Sheet: /

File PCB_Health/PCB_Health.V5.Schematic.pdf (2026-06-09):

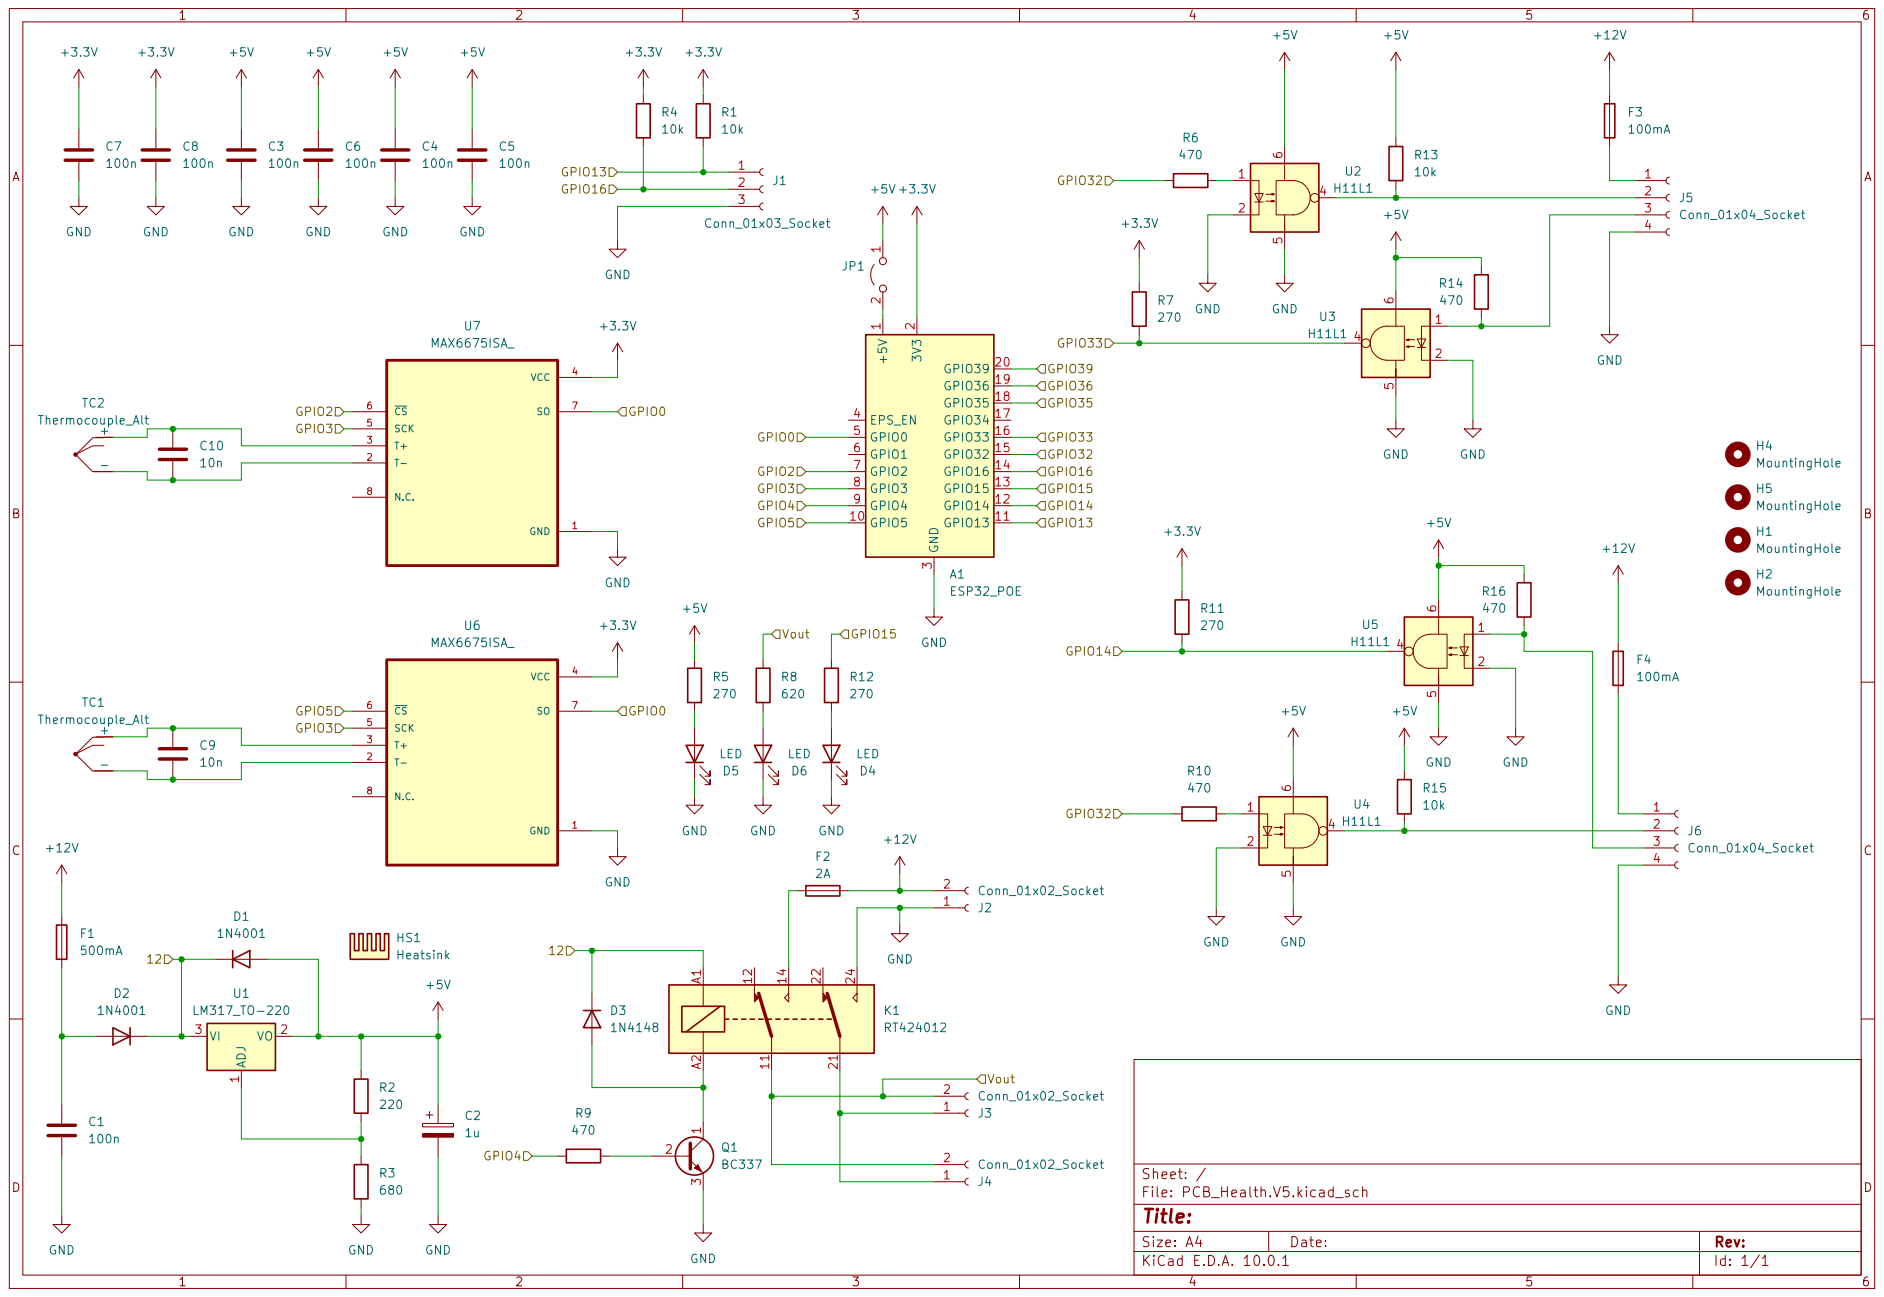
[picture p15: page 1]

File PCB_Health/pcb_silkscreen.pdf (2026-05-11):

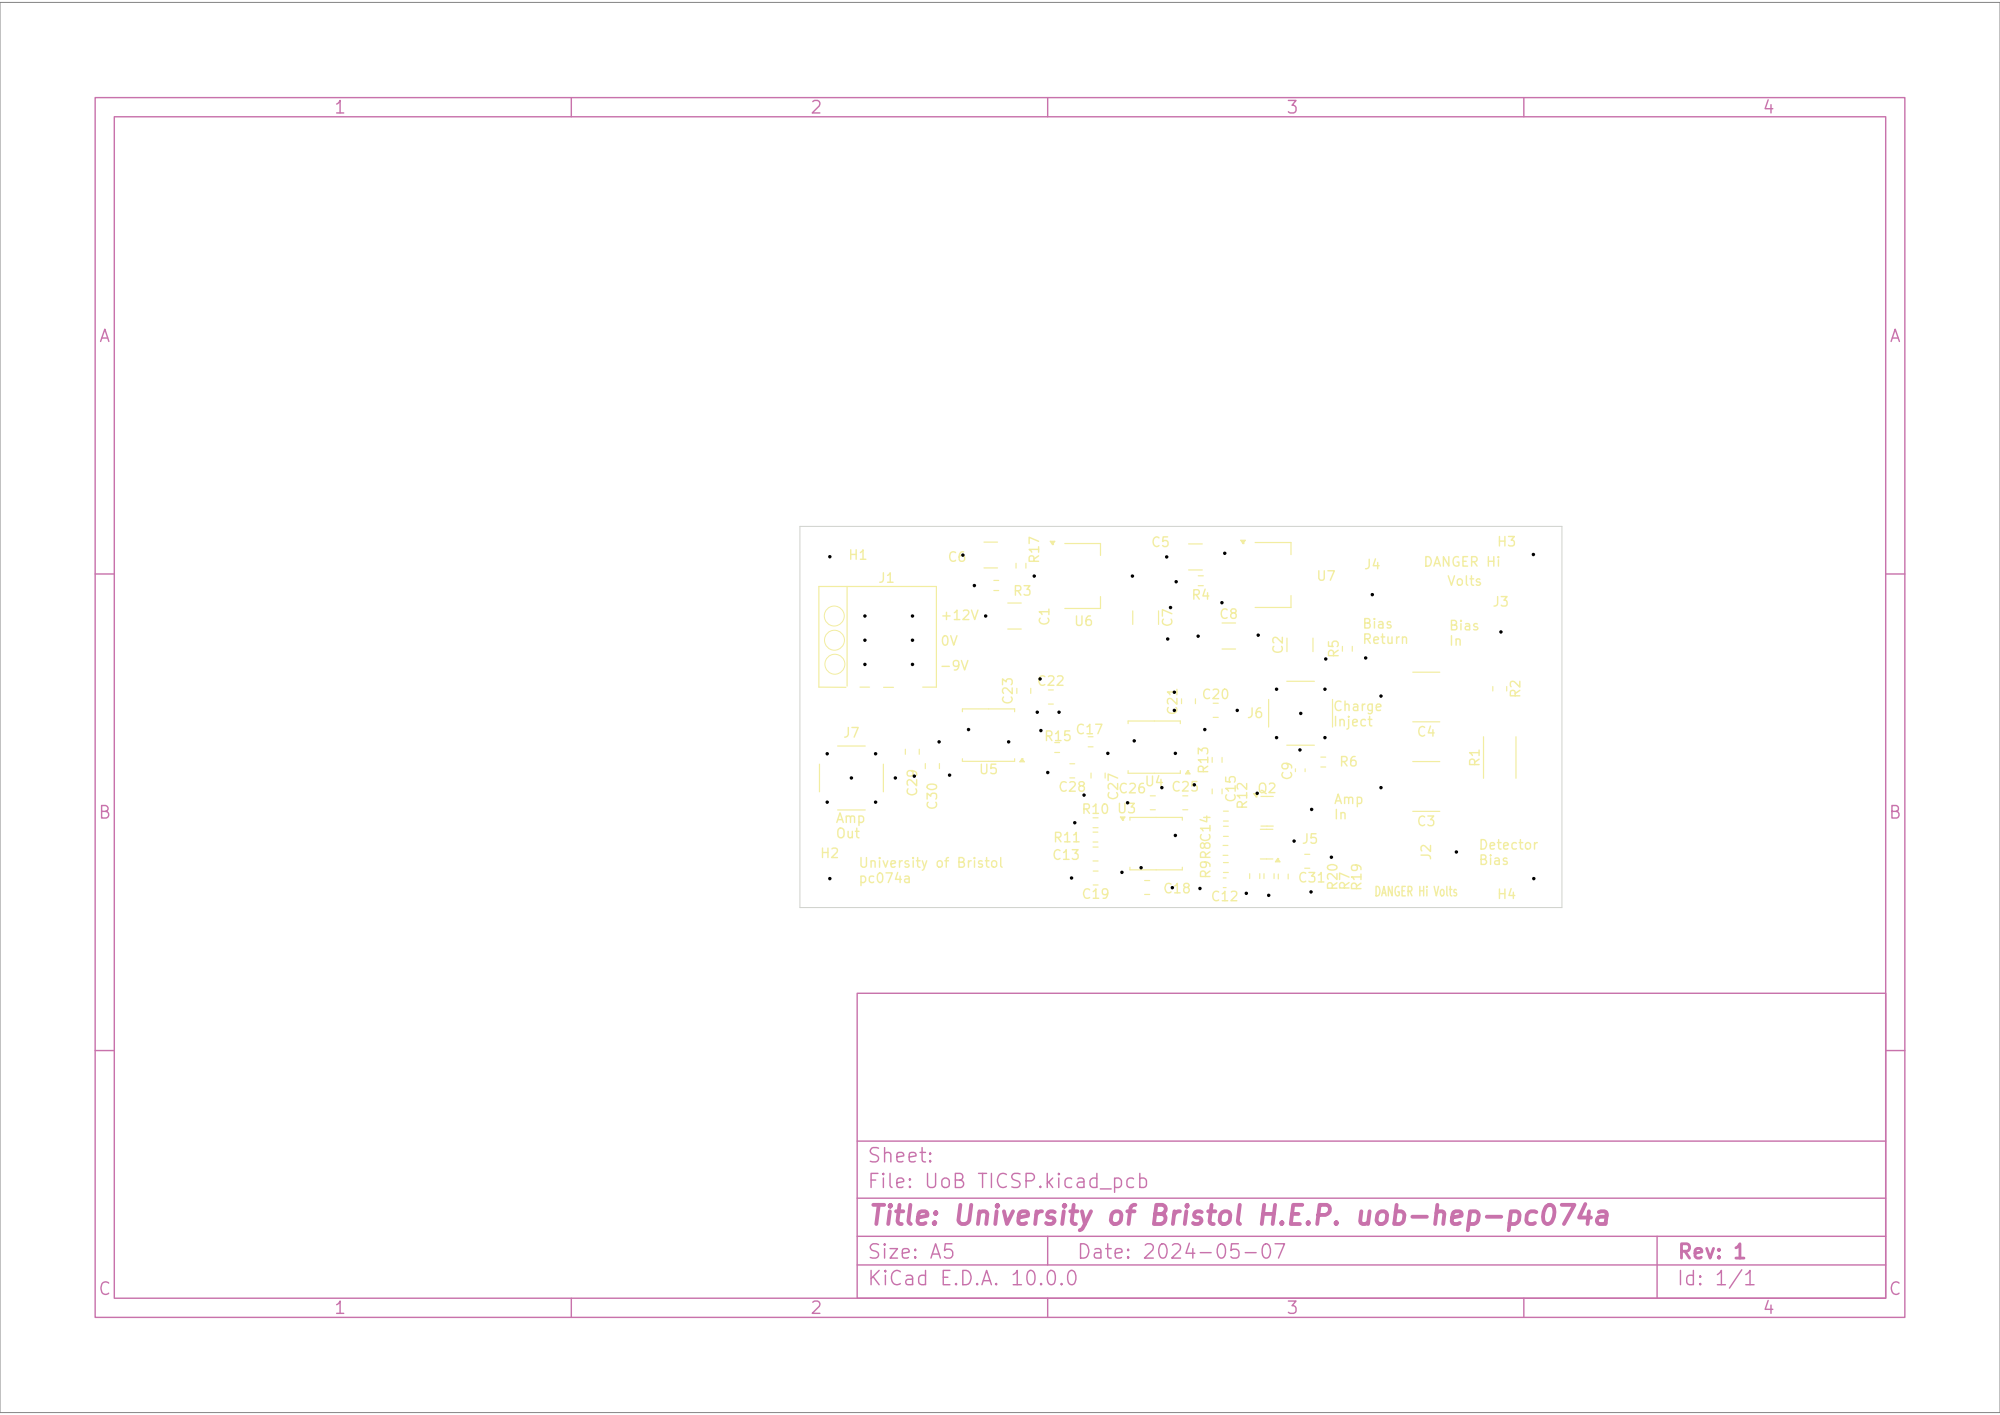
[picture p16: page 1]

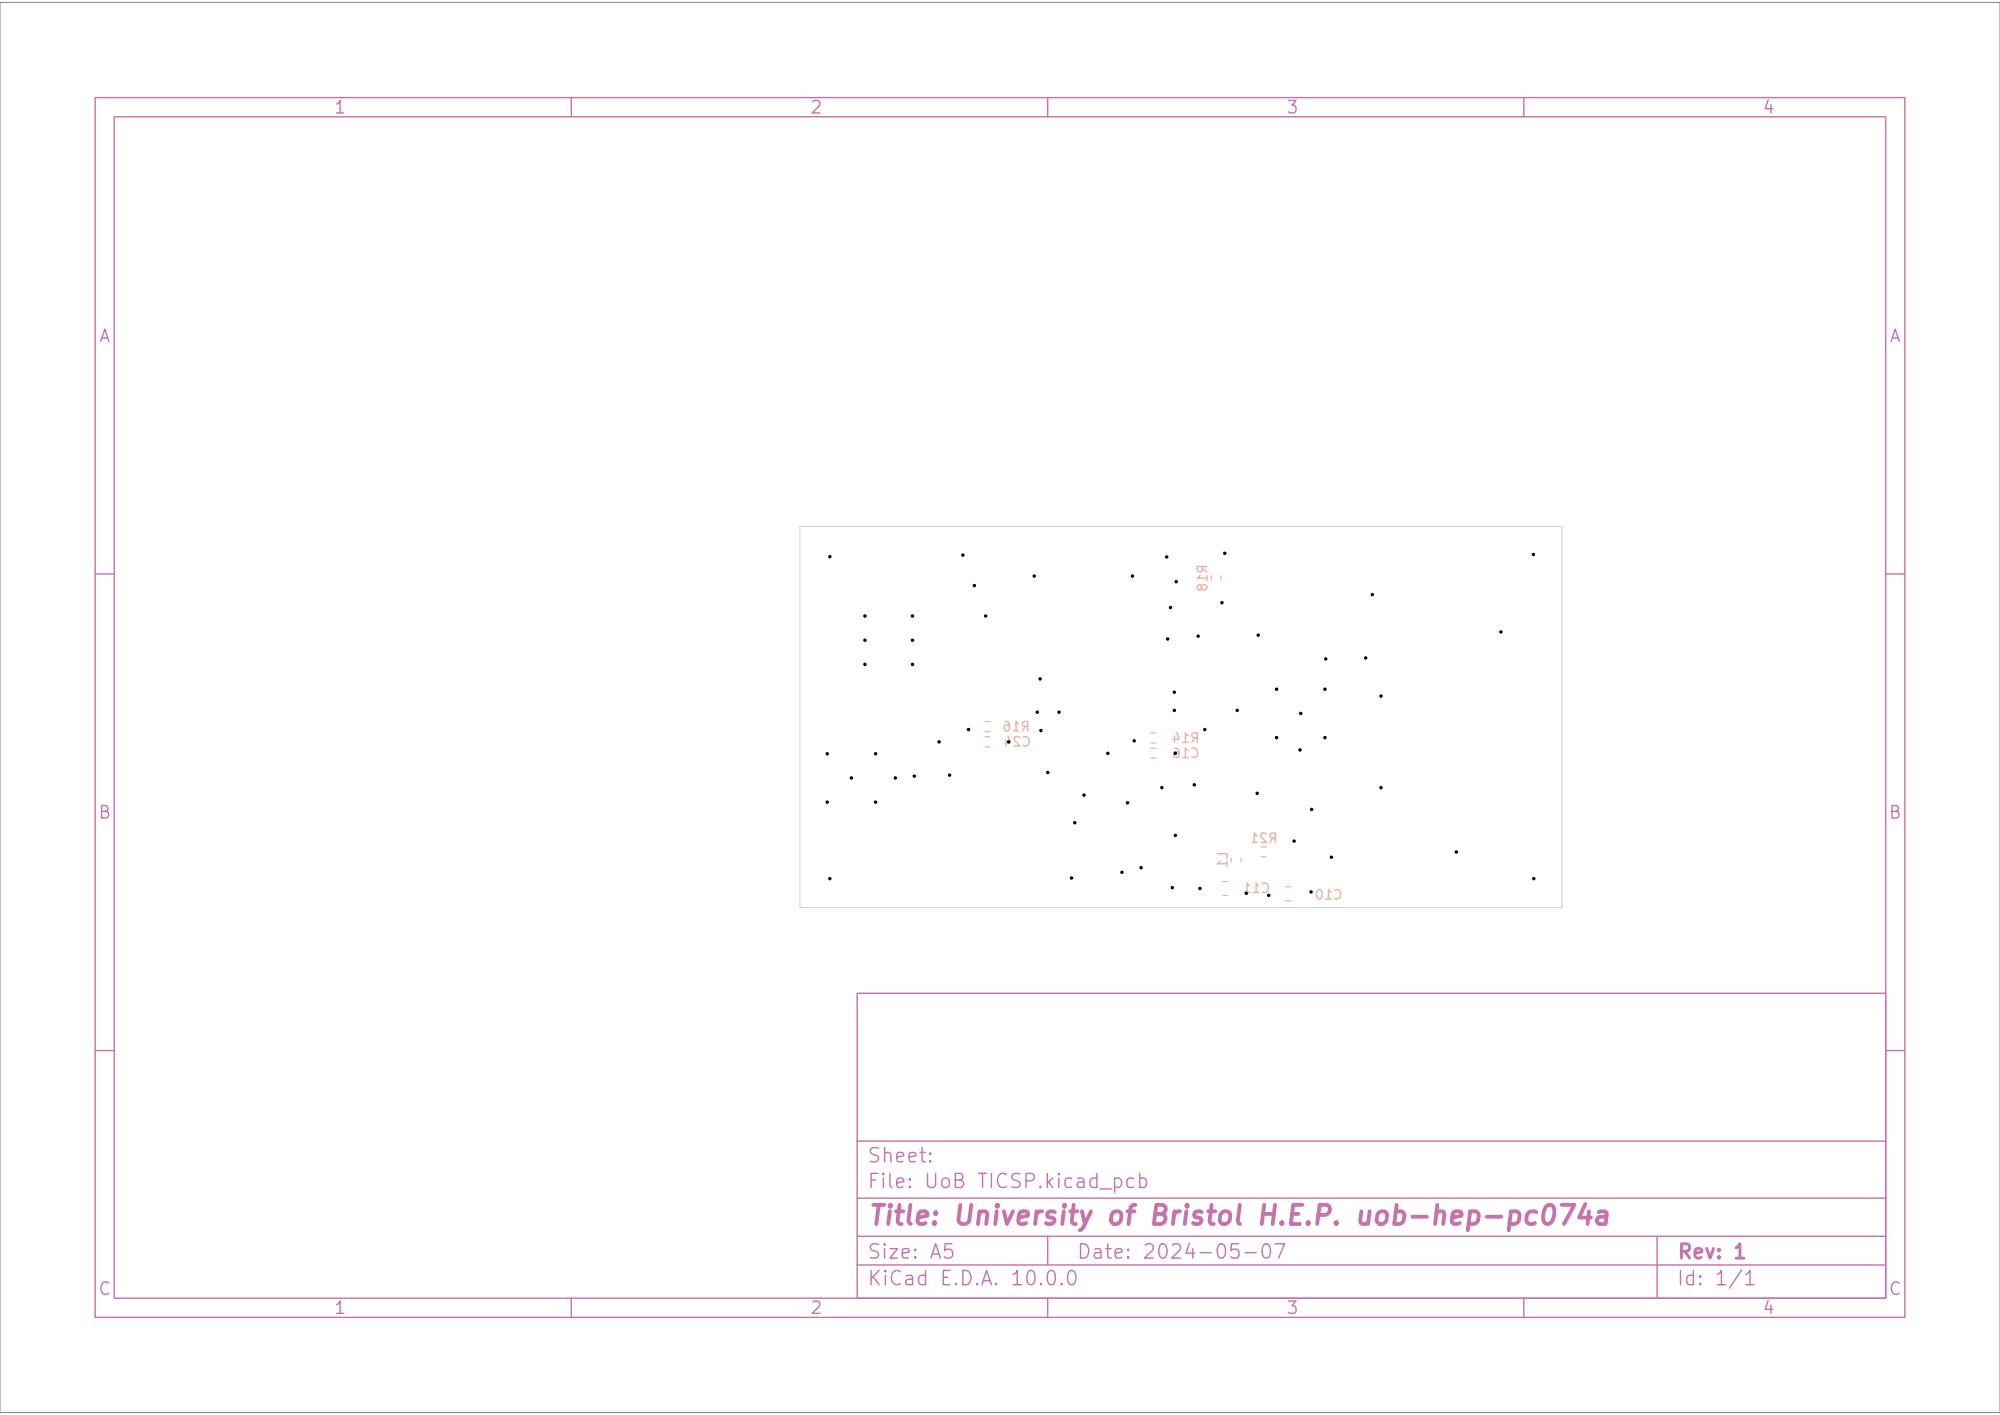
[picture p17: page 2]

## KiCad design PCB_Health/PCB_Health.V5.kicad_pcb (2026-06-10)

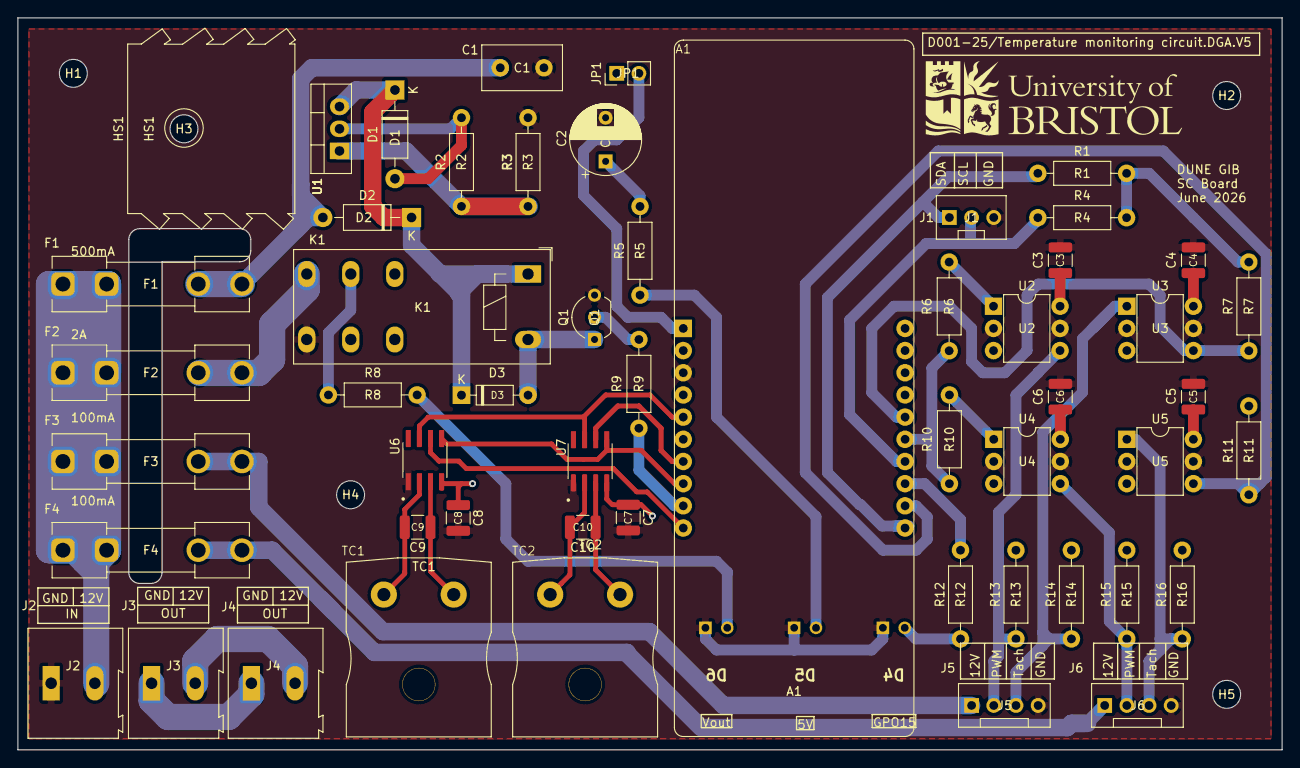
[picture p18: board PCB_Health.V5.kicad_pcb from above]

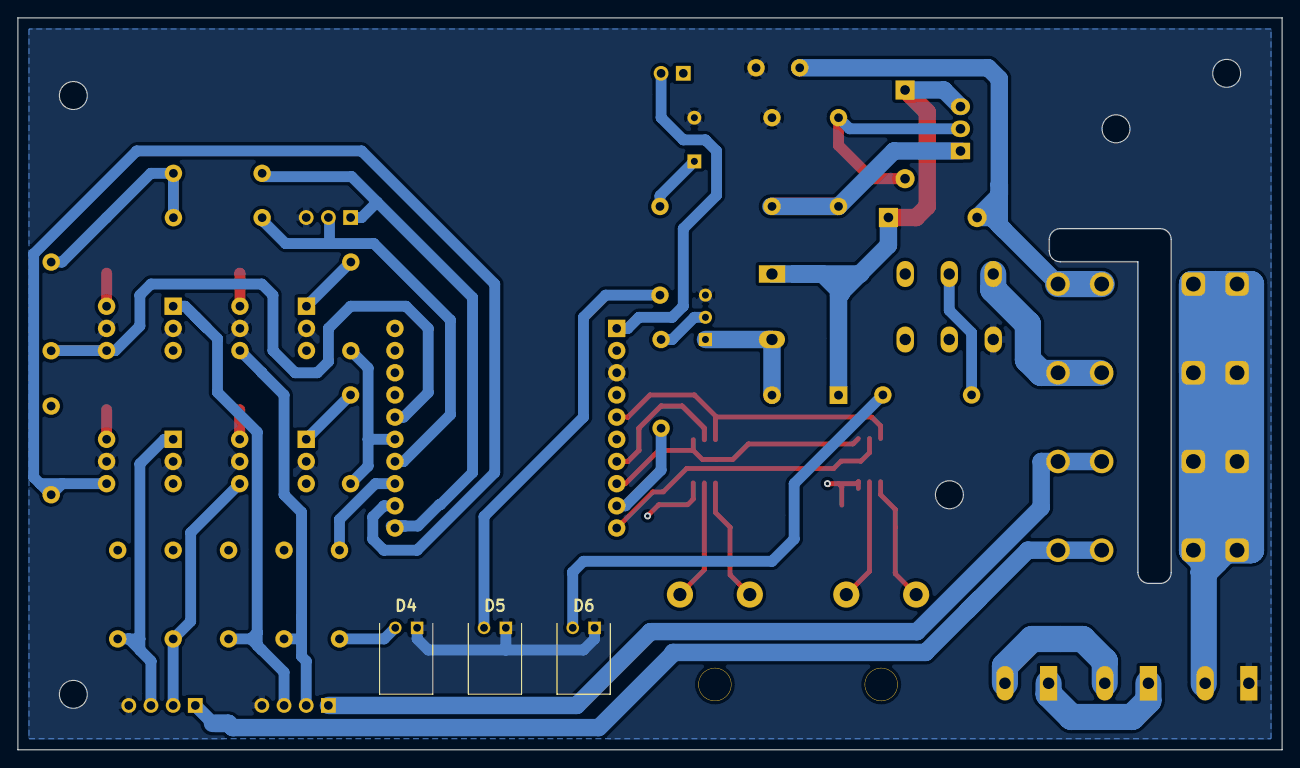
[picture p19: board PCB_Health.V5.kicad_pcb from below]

Board: 4 copper layers, 144.8 x 83.8 mm, 61 parts (3 on the bottom side), 39 nets.

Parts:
A1: ESP32_POE; ESP32-POE-ISO-WROVER
C1: 100n; C_Disc_D9.0mm_W5.0mm_P5.00mm
C2: 1u; CP_Radial_D8.0mm_P5.00mm
C3, C4, C5, C6, C7, C8: 100n; C_1210_3225Metric
C9, C10: 10n; C_1210_3225Metric
D1, D2: 1N4001; D_DO-41_SOD81_P10.16mm_Horizontal
D3: 1N4148; D_DO-35_SOD27_P7.62mm_Horizontal
D4, D5, D6: LED; FLPR60SG
F1: 500mA; Littelfuse 100 Spring Brass, PCB Fuse Clip for 5 x 20 mm Ca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
F2: 2A; Littelfuse 100 Spring Brass, PCB Fuse Clip for 5 x 20 mm Ca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
F3, F4: 100mA; Littelfuse 100 Spring Brass, PCB Fuse Clip for 5 x 20 mm Ca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
H1, H2, H3, H4, H5: MountingHole; MountingHole_3.2mm_M3
HS1: Heatsink; Heatsink_AAVID_TV5G_TO220_Horizontal
J1: Conn_01x03_Socket; PinHeader_1x03_P2.54mm_Vertical
J2, J3, J4: Conn_01x02_Socket; TerminalBlock_Altech_AK300-2_P5.00mm
J5: Conn_01x04_Socket; Mole_KK_1x04__Vertical
J6: Conn_01x04_Socket; PinHeader_1x04_P2.54mm_Vertical
JP1: Jumper_2_Open; PinHeader_1x02_P2.54mm_Vertical
K1: RT424012; Relay_DPDT_Schrack-RT2-FormC_RM5mm
Q1: BC337; TO-92_Inline_Wide
R1, R4, R13, R15: 10k; R_Axial_DIN0207_L6.3mm_D2.5mm_P10.16mm_Horizontal
R2: 220; R_Axial_DIN0207_L6.3mm_D2.5mm_P10.16mm_Horizontal
R3: 680; R_Axial_DIN0207_L6.3mm_D2.5mm_P10.16mm_Horizontal
R5, R7, R11, R12: 270; R_Axial_DIN0207_L6.3mm_D2.5mm_P10.16mm_Horizontal
R6, R9, R10, R14, R16: 470; R_Axial_DIN0207_L6.3mm_D2.5mm_P10.16mm_Horizontal
R8: 620; R_Axial_DIN0207_L6.3mm_D2.5mm_P10.16mm_Horizontal
TC1, TC2: Thermocouple_Alt; Thermocouple Connector
U1: LM317_TO-220; TO-220-3_Vertical
U2, U3, U4, U5: H11L1; DIP-6_W7.62mm
U6, U7: MAX6675ISA_; SOIC127P600X175-8N

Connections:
+3.3V: A1.2 (3V3), C7.1, C8.1, R1.1, R4.1, R7.2, R11.2, U6.4 (VCC), U7.4 (VCC)
+5V: C2.1, C3.1, C4.1, C5.1, C6.1, D1.2 (A), JP1.1 (A), R2.2, R5.2, R13.2, R14.2, R15.2, R16.2, U1.2 (VO), U2.6, U3.6, U4.6, U5.6
+12V: F1.1, F2.1, F3.1, F4.1, J2.2
/12: D1.1 (K), D2.1 (K), D3.1 (K), K1.A1, U1.3 (VI)
/GPIO0: A1.5 (GPIO0), U6.7 (SO), U7.7 (SO)
/GPIO2: A1.7 (GPIO2), U7.6 (~CS)
/GPIO3: A1.8 (GPIO3), U6.5 (SCK), U7.5 (SCK)
/GPIO4: A1.9 (GPIO4), R9.1
/GPIO5: A1.10 (GPIO5), U6.6 (~CS)
/GPIO13: A1.11 (GPIO13), J1.1, R1.2
/GPIO14: A1.12 (GPIO14), R11.1, U5.4
/GPIO15: A1.13 (GPIO15), R12.2
/GPIO16: A1.14 (GPIO16), J1.2, R4.2
/GPIO32: A1.15 (GPIO32), R6.2, R10.2
/GPIO33: A1.16 (GPIO33), R7.1, U3.4
/Vout: J3.2, J4.2, K1.11, R8.2
GND: A1.3 (GND), C1.2, C2.2, C3.2, C4.2, C5.2, C6.2, C7.2, C8.2, D4.1 (K), D5.1 (K), D6.1 (K), J1.3, J2.1, J5.4, J6.4, K1.24, Q1.3 (E), R3.2, U2.2, U2.5, U3.2, U3.5, U4.2, U4.5, U5.2, U5.5, U6.1 (GND), U7.1 (GND)
unnamed: A1.1 (+5V), JP1.2 (B)
unnamed: D3.2 (A), K1.A2, Q1.1 (C)
unnamed: D6.2 (A), R8.1
unnamed: D5.2 (A), R5.1
unnamed: D4.2 (A), R12.1
unnamed: C1.1, D2.2 (A), F1.2
unnamed: F2.2, K1.14
unnamed: J3.1, J4.1, K1.21
unnamed: F3.2, J5.1
unnamed: J5.2, R13.1, U2.4
unnamed: J5.3, R14.1, U3.1
unnamed: F4.2, J6.1
unnamed: J6.2, R15.1, U4.4
unnamed: J6.3, R16.1, U5.1
unnamed: Q1.2 (B), R9.2
unnamed: R6.1, U2.1
unnamed: R10.1, U4.1
unnamed: C9.1, TC1.1 (+), U6.3 (T+)
unnamed: C9.2, TC1.2 (-), U6.2 (T-)
unnamed: C10.1, TC2.1 (+), U7.3 (T+)
unnamed: C10.2, TC2.2 (-), U7.2 (T-)
unnamed: R2.1, R3.1, U1.1 (ADJ)

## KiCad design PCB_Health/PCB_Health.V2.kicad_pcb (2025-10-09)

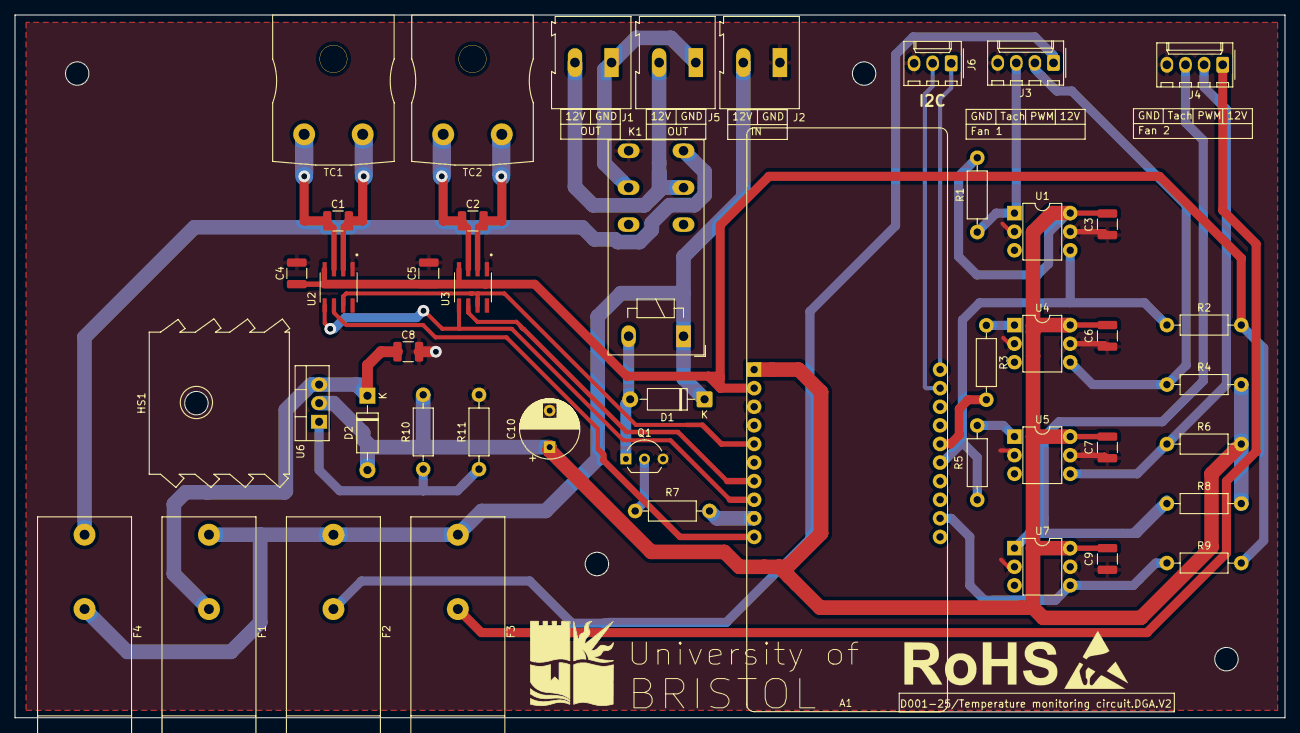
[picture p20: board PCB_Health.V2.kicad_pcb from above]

Board: 4 copper layers, 173.5 x 96.0 mm, 51 parts (0 on the bottom side), 33 nets.

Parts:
A1: ESP32_POE; ESP32-POE-ISO-WROVER
C1, C2: 10n; C_1210_3225Metric
C3, C4, C5, C6, C7, C8, C9: 100n; C_1210_3225Metric
C10: 1u; CP_Radial_D8.0mm_P5.00mm
D1, D2: 1N4001; D_DO-41_SOD81_P10.16mm_Horizontal
F1: 500mA; Fuseholder_Cylinder-5x20mm_Bulgin_FX0457_Horizontal_Closed
F2, F3: 100mA; Fuseholder_Cylinder-5x20mm_Bulgin_FX0457_Horizontal_Closed
F4: 3A; Fuseholder_Cylinder-5x20mm_Bulgin_FX0457_Horizontal_Closed
H1, H1#2, H2, H3, H4: MountingHole; MountingHole_3.2mm_M3
HS1: Heatsink; Heatsink_AAVID_TV5G_TO220_Horizontal
J1, J2, J5: Conn_01x02_Socket; TerminalBlock_Altech_AK300-2_P5.00mm
J3, J4: Conn_01x04_Socket; Molex_KK-254_AE-6410-04A_1x04_P2.54mm_Vertical
J6: Conn_01x03_Pin; Molex_KK-254_AE-6410-03A_1x03_P2.54mm_Vertical
K1: RT424012; Relay_DPDT_Schrack-RT2-FormC_RM5mm
Q1: BC337; TO-92_Inline_Wide
R1, R3, R5, R7, R8: 470; R_Axial_DIN0207_L6.3mm_D2.5mm_P10.16mm_Horizontal
R2, R4, R6, R9: 270; R_Axial_DIN0207_L6.3mm_D2.5mm_P10.16mm_Horizontal
R10: 220; R_Axial_DIN0207_L6.3mm_D2.5mm_P10.16mm_Horizontal
R11: 680; R_Axial_DIN0207_L6.3mm_D2.5mm_P10.16mm_Horizontal
TC1, TC2: Thermocouple_Alt; Thermocouple Connector
U1, U4, U5, U7: H11L1; DIP-6_W7.62mm
U2, U3: MAX6675ISA_; SOIC127P600X175-8N
U6: LM317_TO-220; TO-220-3_Vertical

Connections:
+3.3V: A1.2 (3V3), C4.1, C5.1, R2.2, R9.2, U2.4 (VCC), U3.4 (VCC)
+5V: A1.1 (+5V), C3.1, C6.1, C7.1, C9.1, C10.1, D2.2 (A), R1.2, R4.2, R6.2, R8.2, R10.2, U1.6, U4.6, U5.6, U6.2 (VO), U7.6
+12V: D1.1 (K), F1.1, F2.1, F3.1, F4.2, J2.2, K1.A1
/GPIO0: A1.5 (GPIO0), U2.7 (SO), U3.7 (SO)
/GPIO2: A1.7 (GPIO2), U3.6 (~CS)
/GPIO3: A1.8 (GPIO3), U2.5 (SCK), U3.5 (SCK)
/GPIO4: A1.9 (GPIO4), R7.1
/GPIO5: A1.10 (GPIO5), U2.6 (~CS)
/GPIO14: A1.12 (GPIO14), R9.1, U7.4
/GPIO32: A1.15 (GPIO32), R2.1, R5.2, U1.4
/GPIO33: A1.16 (GPIO33), R3.2
/GPIO36: A1.19 (GPIO36), J6.2
/GPIO39: A1.20 (GPIO39), J6.1
GND: A1.3 (GND), C3.2, C4.2, C5.2, C6.2, C7.2, C8.2, C9.2, C10.2, J2.1, J3.4, J4.4, J6.3, K1.24, Q1.3 (E), R11.2, U1.2, U1.5, U2.1 (GND), U3.1 (GND), U4.2, U4.5, U5.2, U5.5, U7.2, U7.5
unnamed: D1.2 (A), K1.A2, Q1.1 (C)
unnamed: C8.1, D2.1 (K), F1.2, U6.3 (VI)
unnamed: F4.1, K1.14
unnamed: J1.1, J5.1, K1.21
unnamed: J1.2, J5.2, K1.11
unnamed: F2.2, J3.1
unnamed: J3.2, R4.1, U4.4
unnamed: J3.3, R1.1, U1.1
unnamed: F3.2, J4.1
unnamed: J4.2, R6.1, U5.4
unnamed: J4.3, R8.1, U7.1
unnamed: Q1.2 (B), R7.2
unnamed: R3.1, U4.1
unnamed: R5.1, U5.1
unnamed: C1.1, TC1.1 (+), U2.3 (T+)
unnamed: C1.2, TC1.2 (-), U2.2 (T-)
unnamed: C2.1, TC2.1 (+), U3.3 (T+)
unnamed: C2.2, TC2.2 (-), U3.2 (T-)
unnamed: R10.1, R11.1, U6.1 (ADJ)

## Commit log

2023-09-20 Initial commit. About to replace all GIB v6 content
    [GPS_INTERFACE_BOARD-DRCS-Report.csv, GPS_INTERFACE_BOARD.DSN, GPS_INTERFACE_BOARD2.xlsx, GPS_INTERFACE_BOARDv1.brd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]
2023-09-20 Added ACLK SFP block and placed in SFP Interface block. Exported to Allegro. No disaster yet (probably)
    [GPS_INTERFACE_BOARD.DSN]
2023-09-20 Removed ADN2814 from SFP block. Created ACLK interface block ( needed editing. Updated gps_interface_boardv37.brd
    [GPS_INTERFACE_BOARD.DSN]
2023-09-20 Added 1:2 LVDS fanout on ACLK SFP. Started to connect ACLK SFP lines
    [GPS_INTERFACE_BOARD.DSN]
2023-09-20 Problems with export to PCB. Error about U1=1
    [GPS_INTERFACE_BOARD.DSN]
2023-09-20 Rolling back seems to have allowed sucessful export to allegro/gps_interface_boardv37.brd
    [GPS_INTERFACE_BOARD.DSN]
2023-09-21 Connected up ACLK_SFP_{SCL,SDA}
    [GPS_INTERFACE_BOARD.DSN]
2023-09-21 Added reference clock for ACLK link
    [GPS_INTERFACE_BOARD.DSN]
2023-09-21 Correcting net name
    [GPS_INTERFACE_BOARD.DSN]
2023-09-21 FInished ref oscillator, but have unconnected pins. Starting debuggign...
    [GPS_INTERFACE_BOARD.DSN]
2023-09-21 Deleted GBTCLK from FMC netgroup
    [GPS_INTERFACE_BOARD.DSN]
2023-09-21 Online DRC shows very many single pin nets. Baffling
    [GPS_INTERFACE_BOARD.DSN]
2023-09-21 Changed EEPROM to be on main I2C bus. Get same netlist error as previously
    [GPS_INTERFACE_BOARD.DSN]
2023-09-21 Closed Capture an reopened. Was able to export to PCB after reopen. Changed resistor values on ACLK SFP and CDR
    [GPS_INTERFACE_BOARD.DSN]
2023-09-21 Changed resistor values on GIB-MIB SFPs
    [GPS_INTERFACE_BOARD.DSN]
2023-09-21 Changed U50,U51 to have 3.3V (rather than 3.3/5V switchable
    [GPS_INTERFACE_BOARD.DSN]
2023-09-21 Changed U47 from sn74avc2t45 --> sn74lvc
    [GPS_INTERFACE_BOARD.DSN]
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2023-09-21 Got error updating PCB. Exited Capture. Will commit and restart capture
    Details: This error is displayed while running Design Differences. The error occurs due to the equal to ("=") operator being used in the reference designator (LOCATION property) value on a component.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
    ERROR(SPCODD-47): Packaging cannot be completed because the file c:\spb_data\gps_interface_board\allegro\pstxnet.dat could not be loaded. There might be syntax errors in this file. Ensure that the sy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
    ERROR(SPCODD-383): Error at line 8809 in file c:\spb_data\gps_interface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
    [GPS_INTERFACE_BOARD.DSN]
2023-09-21 Added Aux-IO connector. Removed LEDs from main board that will be moved to front panel DB. Started to change sn74lvc from dct package to dcu
    [GPS_INTERFACE_BOARD.DSN]
2023-09-21 Allegro crashed. Ran DBDoctor. About to try export to PCVB again
    [GPS_INTERFACE_BOARD.DSN]
2023-09-21 Re-ran export to PCB after Allegro crash. Seemed to work OK. Have replaced barrel connector with 4-pin ATX-style 12V PC connector. Removed switch. Exported OK
    [GPS_INTERFACE_BOARD.DSN]
2023-09-21 Added fuse to fan power supply lines
    [GPS_INTERFACE_BOARD.DSN]
2023-09-22 Looked over schematics to make list of items to check. Added test-points to ACLK SFP I2C. Marked one of the two resistors feeding 5/3.3V level translator as DNP. Connected up enable line on Y1 (lines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
    [GPS_INTERFACE_BOARD.DSN]
2023-09-22 Updated ROOM property on components in SFP block
    [GPS_INTERFACE_BOARD.DSN]
2023-09-22 Added ACLK_SFP ROOM propert
    [GPS_INTERFACE_BOARD.DSN]
2023-09-22 Created module (Place Replicate Create) and applied to the 6 SFPs@
    [GPS_INTERFACE_BOARD.DSN]
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2024-08-28 Synchronized design. Down-rev to v17.4 on /gps_interface_boardv40_quickplaced_downreved.brd
    [GPS_INTERFACE_BOARD.DSN]
2024-08-29 Edited block diagram on first page. Printed out schematics
    [GPS_INTERFACE_BOARD.DSN]
2024-08-29 Printed out schematics (after some considerable effort: Select top level design and use occurance mode to get correct refdes). Removed the Storage pages - which were just a dumping ground for unfinis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
    [GPS_INTERFACE_BOARD.DSN]
2024-09-02 adjusted board file for colour preference
    [GPS_INTERFACE_BOARD.DSN]
2024-09-05 Sourced footprint for J17 - but unable to find in schematic at moment
    Also exported all footprints/pads from Allegro board file database and set up search paths to look in dedicated folder. The RJ45 used for J17 was sourced via mouser and mapped to the pin labels being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
    [172448-yy04.psm, 22-23-2031.psm, 5025983993.psm, 6-2301994-2.stp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]
2024-09-05 ignore last message - found RJ45 from older board file
    Happier with source now, everything else true from previous
    [_te_6-2301994-2.psm, te_6-2301994-2.psm]
2024-09-06 mounting hole position rework
    [samtec_asp-134606-01.psm, x_samtec_asp-134606-01.psm]
2024-09-19 New board stack up - lots of routing needs to be redone due to new width/sep on 100r diff trace
    [pcbtrain_build.xlsx, qfn50p300x300x90-17n.psm]
2024-09-27 some footprint tweaks - odd padstack origins?!
    Almost there with component placement, need to assess overall layout placement soon. Routing is getting there.
    [son65p300x300x100-9n-d.psm]
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2024-10-29 Editing pins for Si5021 . Edited net names for 2.5V regulators
    [GPS_INTERFACE_BOARD.DSN]
2024-10-29 Merged Pete's changes from PR31
    [172448-yy04.psm, 22-23-2031.psm, 5025983993.psm, 6-2301994-2.stp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]
2024-10-31 Fixed some typos in the schematic comments. Got rid of two only-one-pin-on-the net instances (on PLL output power pin and PGOOD from P5V5 regulator. Printed schematics. Produced a down-reved board fo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
    [GPS_INTERFACE_BOARD.DSN]
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2024-11-13 Need help visualising the connector mating
    I have repositioned the mounting holes on that connector but I am having a hard time visualising it mated. I have based the locations on the pc069b board file you sent to me. I believe it is correct 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
    [dune_outline.dxf, pc069b_toplevel_18bare.brd, samtec_asp-134606-01.psm]
2025-01-13 Adding Pete's final board that was sent for production, together with the ODB++ export from it
    [GPS_INTERFACE_BOARD.DSN]
2025-07-04 Committing files before starting to address issues
    [6-2301994-2.stp, GNP1150TCA-ZE2.stp, GPS_INTERFACE_BOARD-DRCS-Report.csv, GPS_INTERFACE_BOARD2.xlsx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]
2025-07-04 Fixed schematic errors in 2.5V and 3.3V power rails
    [GPS_INTERFACE_BOARD.DSN]
2025-07-04 Marked relevant DNP resistors on 2.5 and 3.3V . Exported to PCB - N.B. changed r resistors became unplaced. May be disconnected. Exported placement before export to get placement back. Adding BoM for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
    [GPS_INTERFACE_BOARD.DSN, gps_interface_boardv53ph_BOM.xls]
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2025-07-07 Changed UID PROM I2C address from 0x50 --> 0x54
    [GPS_INTERFACE_BOARD.DSN]
2025-07-08 Schematic edited to change SCL0/SDA0 to SCL_PLR/SDA_PWR on temp/voltage/current I2C monitors
    [GPS_INTERFACE_BOARD.DSN]
2025-07-08 Completed schematic changes to move temp/current/voltage I2C monitors
    [GPS_INTERFACE_BOARD.DSN]
2025-07-08 Moved PLL to FPGA I2C bus. Added 0.1inch header and zero ohm resistors to disconnect for debugging
    [GPS_INTERFACE_BOARD.DSN]
2025-07-08 Moved SFP_LOS lines to FPGA on schematic. Kept TX_FLT on I2C extender. PCB needs routing
    [GPS_INTERFACE_BOARD.DSN]
2025-07-09 Changed level translator for one that was already on the board. Export to t PCB. PCB needs layout
    [GPS_INTERFACE_BOARD.DSN]
2025-07-09 Swapped A<-->B on U17 so that VCCA < VCCB
    [GPS_INTERFACE_BOARD.DSN]
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2025-07-09 Replaced ADN2814 with ADN2817 ( ADN2818 not recommended for new designs). Exported to PCB. Needs layout
    [GPS_INTERFACE_BOARD.DSN]
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2025-07-10 Replaced OR gate with fussy resistor network for LOS/TX_FAULT RED/GREEN with dual buffer with one LED on each output
    [GPS_INTERFACE_BOARD.DSN]
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2025-07-14 Replaced device specific zero ohm links connecting SCL/A_PWR with generic 0603 zero ohm links. Ref des updated to R3699/R3700. See https://github.com/uob-hep-cad/upenn-dune-gib/issues/40
    [GPS_INTERFACE_BOARD.DSN]
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2025-07-22 Corrected SCH around U110 - Connected pins 2, 10, & 12 to Vcc. Layout updates WIP
    [GPS_INTERFACE_BOARD.DSN]
2025-07-22 U110 Routed. All DRCs cleared except issues with constraints for Sig layer Diff Pairs
    [GPS_INTERFACE_BOARD.DSN]
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2025-07-31 rotated TX_FAULT and CDS_LOL LEDs. Corrected in SCH and BRD. Tidied up silkscreens and assy dwgs to match
    [GPS_INTERFACE_BOARD.DSN]
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2025-08-13 Editing BoM to format for PCBTrain upload tool. And addressing numerous issues - see GitHub issues log. Still WIP
    [BoM-condensed.xlsx, BoM-edited for PCB Train.xlsx, BoM-individual lines.xlsx, pcb-bom-sample-file.xlsx]
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2025-08-20 Removed LTC6957 from GPS clock input and replaced with LTC6954 comparator and LVDS fanout. Will change IRIGB input to use the same comparator
    [GPS_INTERFACE_BOARD.DSN]
2025-08-20 Proof-of-concept layout of replacing LTC6957 iwth LTC6754 (https://github.com/uob-hep-cad/upenn-dune-gib/issues/67), removed redundant vcc3v3_lfilt ( https://github.com/uob-hep-cad/upenn-dune-gib/iss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
    [GPS_INTERFACE_BOARD.DSN]
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
